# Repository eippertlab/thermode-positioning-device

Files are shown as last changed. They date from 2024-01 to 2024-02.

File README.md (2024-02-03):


 
[][cc-by]
# ThermoSlide: an MR-compatible thermode positioning device

## Purpose
The ThermoSlide presented here allows the thermode Medoc PATHWAY CHEPS (https://www.medoc-web.com/pathway-model-cheps) to be placed and repositioned on the forearm of a participant in an MRI scanner remotely, without having to move the participant or the scanner table, and with easier access compared to reaching into the scanner bore.

## Construction
Two coaxial PVC tubes (rigid conduit EN16 and EN20) and a 3D-printed holder are used for this purpose. The holder consists of four parts that are screwed together (4 pcs. M4 x 12 countersunk flat head, 4 pcs. M3 x 12 slotted cheese head). The inner “fixed” tube (length: 136cm) is firmly attached to Part_2 of the holder using two M3 x 25 screws and nuts. The movable outer tube (length: 121cm) has a bobbin at the end, and an elastic band that can be tightened or loosened by rotating it. Both flanges of the bobbin have cut-outs on the end faces into which an M3 screw will fit. This is used to lock the bobbin in place by shifting the outer tube longitudinally when the elastic strap is tightened sufficiently.

During assembly, the elastic band (size: 3.5cm x 50cm) must first be threaded through the two slits in the bobbin and then sewn into a loop. The bobbin can then be plugged onto the movable tube and secured with two M2 x 8 brass screws. To reduce the friction with the elastic band, an accordingly punched out PTFE foil (approx. 90mm x 40mm x 0.3mm) can be wrapped around the center bar of Part_1 and then fixed from below with four M3 x 4 screws.

Optionally, the ThermoSlide can be equipped with a simple torque gauge (as done here), allowing one to apply approximately the same pressure when repositioning the thermode to another part of the forearm. The main component is a special 3D printed torsion spring. The end with the angle indicators is attached to the moving tube with three M4 x 12 screws. At the other end, three 120° spaced pointers and a short handle tube (EN25 rigid conduit) are screwed on.

The torsion spring was fabricated from KEYENCE AR-M2 at a local service provider. All other components were printed on a Stratasys Eden260VS 3D printer. The material used was MED610. Nylon screws are used unless otherwise noted.

## Usage, citation and contact
We have used this device in various fMRI studies at 3T and 7T (e.g. https://www.biorxiv.org/content/10.1101/2023.12.22.572825v1) and would be happy to provide help in case you are interest in using such a device as well. In case you use this device, please cite it as shown under 'Cite this repository' on the right. If you have any questions, please feel free to reach out to rmueller@cbs.mpg.de. 

## License
This work is licensed under a
[Creative Commons Attribution 4.0 International License][cc-by].

[][cc-by]

[cc-by]: http://creativecommons.org/licenses/by/4.0/
[cc-by-image]: https://i.creativecommons.org/l/by/4.0/88x31.png
[cc-by-shield]: https://img.shields.io/badge/License-CC%20BY%204.0-lightgrey.svg

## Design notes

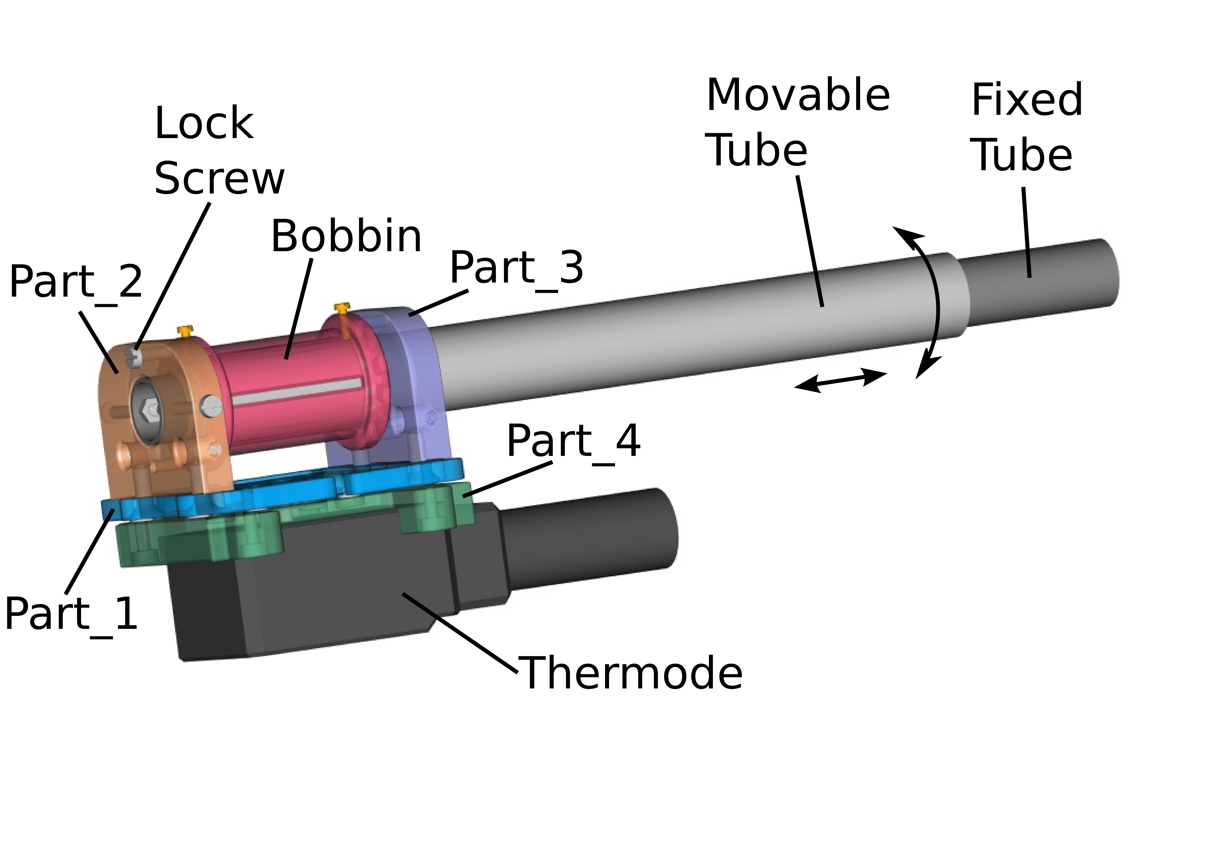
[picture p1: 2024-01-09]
thermodeFixationDevice.png

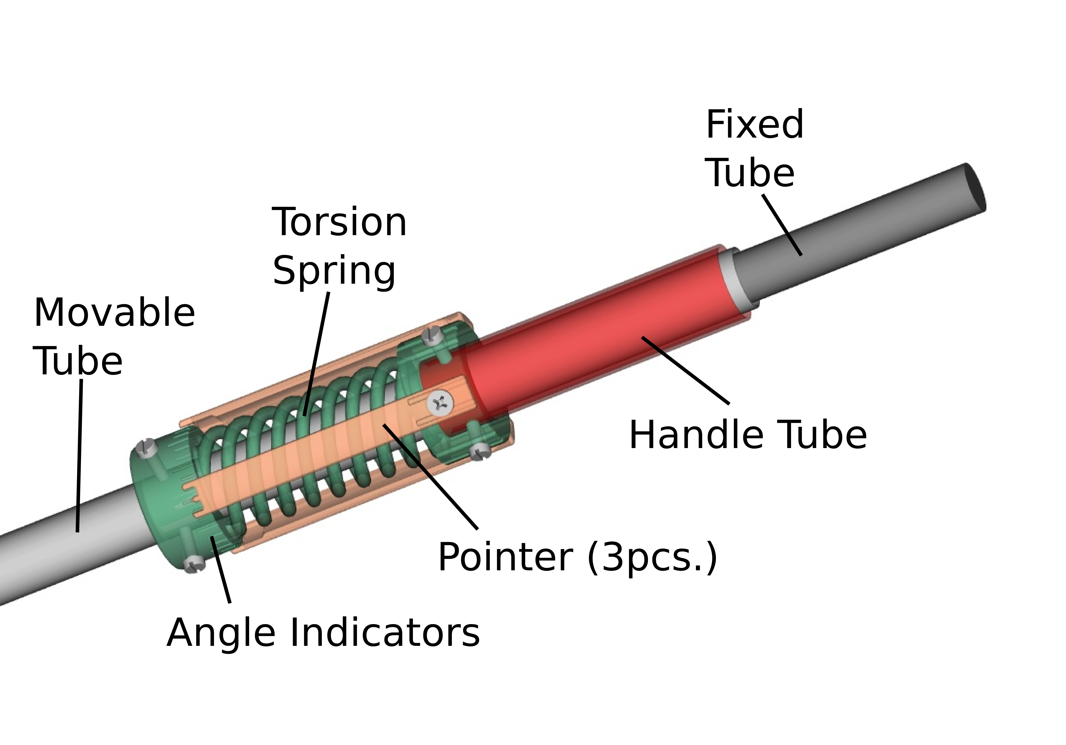
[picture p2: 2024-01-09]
torqueGauge.png

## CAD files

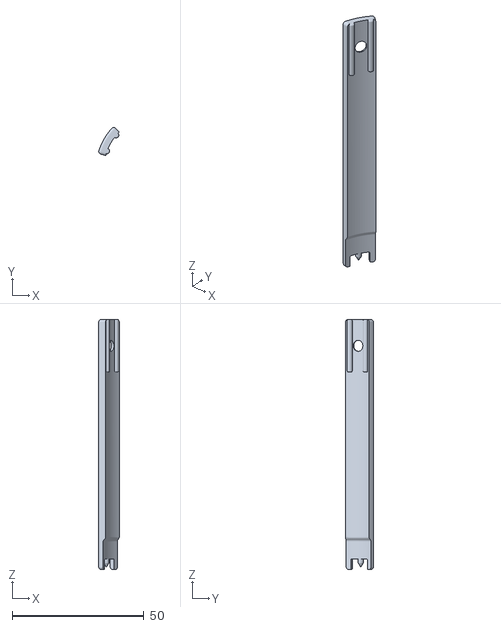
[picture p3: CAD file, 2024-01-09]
pointer.stl
7.83 x 10.7 x 95.0

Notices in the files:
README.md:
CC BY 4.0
